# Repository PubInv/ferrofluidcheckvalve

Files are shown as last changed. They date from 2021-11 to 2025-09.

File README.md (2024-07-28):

# A Passive Ferrofluid Check Valve (PFCV)
This repo describes a *passive* ferrofluid one-way valve.
This invention is apparently novel and should be quite important for making it 
easier to fabricate lab-on-a-chip applications, because it has no moving parts,
and is completely passive.

# Theory Paper

For more than a year, I have been trying to develop a complete theory of the valve.
My somewhat messy efforts are [here](https://github.com/PubInv/ferrofluidcheckvalve/blob/master/doc/EnergyMinimization/passiveFerrofluidCheckValveTheory.pdf) in 
this repo. I tend to write expansively in LaTeX, putting down a lot of thoughts and performing calculations more
verbosely than would be accepted in typical published paper.  This paper should be considered my notes at present,
a "treatise" if you will, rather than a paper being prepared for publication. Some parts of it are likely stale.

# Progress as of 13 July 2024

Last night, Joe Hershberge and proved out our best valve design yet. We are 
now consistently getting a collapse pressure of more than 100 cm of water, 
and cracking pressure of less than 10 cm of water.
This is the best ratio we have measured. 
This design used a 3D chamber,
which was a recommendation that Joe made. 

IMG_5257 (1)

Note, in the data below, we used a high-pressure manometer with a resolution of only 4 cmH2O;
we have a more precise low-pressure one, which we will use in the next experiments.
| Trail Name  | Cracking (cmH2O)  | Collapse (cmH2O)  |  Comment |   |
|---|---|---|---|---|
| X1  | 8 | 114  |   |   |
| X2  | 8  | 110   |   |   |
| X3  | 8  | 110  |   |   |
| X4  | 12  |  106 |   | 2" magnet instead of 1"  |
| X5  |  8 |  110 |   | System held upside down in same configuration  |

  I now believe this a very significant result (in this small technical niche which we created.)

# A Humorous History
Our previous attempts to do this were deeply flawed (see below).

When public invention volunteer Veronica Stuckey agreed to work on this project, 
she invigorated the design effort. I wrote a quick (3-day) simulation using particles
in a magnetic field, which gave me some rough guidance. This allowed
me to design an asymmetric chamber which I thought might work. 
Veronica immediately tested it, and it worked---but in the opposite direction from the
way that I thought it would work!
That is, my theory of why the inlet would have low cracking pressure and the outlet 
sustain high pressure was completely and perfectly backwards. However, this meant
that despite this error, we had succeeded in creating a functional ferrofluid valve
with no moving parts!
-- Robert L. Read

# The Successful Valve

The current valve is described in [the paper](https://github.com/PubInv/ferrofluidcheckvalve/blob/master/doc/journal-1.2/asme2ej.pdf) in this repo that we will
submit to an open access journal soon. Like all Public Invention inventions, we do not seek patents, and you are free to use this design under the CERN Strong Reciprocal License [(CERN-OHL-S-2.0)](https://ohwr.org/cern_ohl_s_v2.txt). 

The gist of the fundamental invention can be understood from the this diagram:
TopViewFerrofluidModelLabelled

Veronica Stuckey made a [nice video](https://www.youtube.com/watch?v=IGzz6LX1n6A) of her work that explains it well.



# Design For a Piston to Make a Pump

One of the most interesting things to do with these valves are to use them to make a pump. A pump simply requires a change in volume in the 
pumped fluid between two valves allowing flow in the same direction. We demonstrate this with our existing appratus via a hand-pumped syringe.
However, we could also use a ferrofluid piston, in which case we would have a pump with no moving parts except for ferrfoluid itself.

A piston may be made by moving a blob of ferrofluid in channel (this has been done by many researchers already.) Based on some initial
experiments, here is our design for an electronic ferrofluid piston:

Pump Improvements

# Initial (Wrong Polarity) Sketch Idea

NOTE: as mentioned before, this idea is wrong, but usefully wrong---the valve works in the opposite direction to what is suggested.

Ferrofluid Check Valve Idea #2

# Future Steps

As always, Public Invention invites you take this idea and run with it! Some potential fun things to do next would be:
1. Can the performance of the valve be improved by shaping the chamber and/or the magnetic field better?
2. How do the pressures change if you scale it down?
3. How far can it be scaled down with a 3D printer before some sort of lithographic or etching technique is required?
4. Can you make a positive-displacement pump on a single unit by making a 3D printed pump consiting of a 2 PFCVS, a piston made out of a ferrofluid bolus, and an external electomagnet to move the piston (possibly on a PCB)?
5. This design is essentially a 2D shape slightly extrudede to be a 3D volume. Is there a fully 3D design that is similar but would have better performance?

# Previously (2019)
An attempt to build a ferrofluidcheckvalve

This project is now considered a failure; I've attempted to write up what was learned, which is [published](https://medium.com/@RobertLeeRead/failed-experiments-with-ferrofluid-742fa13b0ae1) at Medium

# References

Note: The academic paper herein contains a better list of references!

[Micromachines | Free Full-Text | Magnetically Induced Flow Focusing of Non-Magnetic Microparticles in Ferrofluids under Inclined Magnetic Fields | HTML (mdpi.com)](https://www.mdpi.com/2072-666X/10/1/56/htm)

[Ferrofluidic Pumps: A Valuable Implementation Without Moving Parts | IEEE Journals & Magazine | IEEE Xplore](https://ieeexplore.ieee.org/abstract/document/5196729/citations?tabFilter=patents#anchor-patent-citations)

[Modeling of ferrofluid magnetic actuation with dynamic magnetic fields in small channels | SpringerLink](https://link.springer.com/article/10.1007/s10404-014-1442-7)
(This paper was the one talking about the rotating magnets, however, this was all done in COMSOL simulation)

[Development of a novel electromagnetic pump for biomedical applications - ScienceDirect](https://www.sciencedirect.com/science/article/abs/pii/S092442471000049X)

[Magnets & Magnetism Frequently Asked Questions | Magnet FAQs (intemag.com)](https://www.intemag.com/magnetic-frequently-asked-questions)
(This site I referenced because of the portion the talks about how a magnet's strength drops off over distance, and gives a good overview on magnetic behavior for the uninitiated)

[On demand manipulation of ferrofluid droplets by magnetic fields - ScienceDirect](https://www.sciencedirect.com/science/article/abs/pii/S092540051631913X)
(Ferrofluid behavior with magnets, not specific)

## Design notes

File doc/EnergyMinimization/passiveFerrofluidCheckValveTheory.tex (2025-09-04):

%%%%%%%%%%%%%%%%%%%%%%%%%%% asme2ej.tex %%%%%%%%%%%%%%%%%%%%%%%%%%%%%%%
% Template for producing ASME-format journal articles using LaTeX    %
% Written by   Harry H. Cheng, Professor and Director                %
%              Integration Engineering Laboratory                    %
%              Department of Mechanical and Aeronautical Engineering %
%              University of California                              %
%              Davis, CA 95616                                       %
%              Tel: (530) 752-5020 (office)                          %
%                   (530) 752-1028 (lab)                             %
%              Fax: (530) 752-4158                                   %
%              Email: hhcheng@ucdavis.edu                            %
%              WWW:   http://iel.ucdavis.edu/people/cheng.html       %
%              May 7, 1994                                           %
% Modified: February 16, 2001 by Harry H. Cheng                      %
% Modified: January  01, 2003 by Geoffrey R. Shiflett                %
% Use at your own risk, send complaints to /dev/null                 %
%%%%%%%%%%%%%%%%%%%%%%%%%%%%%%%%%%%%%%%%%%%%%%%%%%%%%%%%%%%%%%%%%%%%%%

%%% use twocolumn and 10pt options with the asme2ej format
%% \documentclass[twocolumn,10pt]{asme2ej}
\documentclass{asme2ej}
\usepackage{amsmath}
\usepackage{graphicx} %% for loading jpg figures
\usepackage{hyperref}   % to set up hyperlinks
\hypersetup{
	colorlinks=true,
	linkcolor=blue,
	citecolor=blue,
	urlcolor=blue,
}
\usepackage[square,numbers]{natbib}

\usepackage{float}

\usepackage{outlines}
\usepackage{enumitem}
\setenumerate[1]{label=\Roman*.}
\setenumerate[2]{label=\Alph*.}
\setenumerate[3]{label=\roman*.}
\setenumerate[4]{label=\alph*.}

\newtheorem{conjecture}{Conjecture}
\newtheorem{corollary}{Corollary}
\newtheorem{theorem}{Theorem}

%% The class has several options
%  onecolumn/twocolumn - format for one or two columns per page
%  10pt/11pt/12pt - use 10, 11, or 12 point font
%  oneside/twoside - format for oneside/twosided printing
%  final/draft - format for final/draft copy
%  cleanfoot - take out copyright info in footer leave page number
%  cleanhead - take out the conference banner on the title page
%  titlepage/notitlepage - put in titlepage or leave out titlepage
%
%% The default is oneside, onecolumn, 10pt, final

\title{A Novel Passive Ferrofluid One-way (Check) Valve Based on Energy Minimization}

%%% first author
\author{Robert L. Read
\affiliation{
  Founder, Public Invention\\
  Email: read.robert@pubinv.org
    }
}

%%% second author
%%% remove the following entry for single author papers
%%% add more entries for additional authors
\author{Veronica Stuckey
  \affiliation{
    Biomedical Engineer, University of Texas at Austin \\
    %%Email:  stuckey002@gmail.com
    }
}

%%% third author
%%% remove the following entry for single author papers
%%% add more entries for additional authors
\author{Joe Hershberger
\affiliation{
  Investigator, Public Invention\\
  %%Email: read.robert@gmail.com
    }
}

\begin{document}

\maketitle

%%%%%%%%%%%%%%%%%%%%%%%%%%%%%%%%%%%%%%%%%%%%%%%%%%%%%%%%%%%%%%%%%%%%%%
\begin{abstract}

This work focuses on a novel passive ferrofluid check valve. The structure is free of mechanical moving parts and is based on a ferrofluid plug in a narrow channel.
Check valves, also known as one-way valves, are devices that allow fluids to move in only one direction primarily to prevent backflow in the system.
The valve returns to stasis (closes) under the influence of a static magnetic field when the pressure on the ferrofluid is less than the magnetic forces of the ferrofluid itself.
Here, we present a simple design for a passive, normally closed ferrofluid check valve consisting of a unique channel-and-chamber geometry, a bolus of ferrofluid, and a static magnetic field.
The flow is determined only by the force differential between the pressure of the fluid in the channel and the magnetic force of the ferrofluid at the intersection of the channel and the chamber

Small pumps and valves enable flow management in microfluidic systems.
A novel passive ferrofluid check valve is presented.
The valve consists of only a
unique channel-and-chamber geometry, ferrofluid, and a stationary
magnetic field.
The flow is determined only by the inlet and output pressure,
and the magnetic field is completely static.
The prototype valve and experimental setup are explained
and performance of the valves cracking and collapse pressure reported.
This initial design can be used for microfluid handling and lab-on-a-chip
applications.

Additionaly we present a theory of operation based on energy minimization
and compare predicted performance to actual performance.
\end{abstract}

%%%%%%%%%%%%%%%%%%%%%%%%%%%%%%%%%%%%%%%%%%%%%%%%%%%%%%%%%%%%%%%%%%%%%%
\section{To Do}
\begin{itemize}
\item Fully understand the meaning of the Kelvin Force - This should probably be called a magnetophoretic force,
  or an inverse-magnetophoretic force. It should probably not be called the Kelvin force of the magnetic buoyancy.
  Perhaps we should call it energy minimization buoyancy force.
\item Improve Proof of 2D Manetostatic Blob Minimimization Conjecture
\item Understand Ferrofluid Spikes (a version of Rayleigh-Taylor or (normal-field instability) instability )
\item Prove that theorem that a U-tube cannot make an assymetric valve (yes it is called a U-tube)
  U-tubes obviously make pressure gagues, and this is not dependent on the relative areas,
  though the scale is.
\item Centrifugal force is $ F = m \omega^2 \rho$, where $\rho$ is the distance from the center of the rotating frame of
  reference. So we can make a perfectly linear force in that way.
\item Get magnetohydrodynamics by Rosenweig - $250: https://www.amazon.com/Ferrohydrodynamics-Dover-Books-Physics-Rosensweig/dp/0486678342 There is a Kindle Edition for $20, I should probably buy.
  \item ABSOLUTE MUST: Formulate and prove the perpendicular ferrofluid boundary theorem.
\end{itemize}

\subsection{Writing ToDo}

\begin{itemize}
\item This may be a useful reference: \url{https://hal.science/hal-03416758/document}
\item This is a pump that uses a plug and two check valves: \url{https://www.researchgate.net/publication/37423698_A_ferrofluid_micropump_for_lab-on-a-chip_applications/figures?lo=1}
  \item Write a new section on U-tube theory. Should I use a pen?
  \end{itemize}

\section{Outline}

\begin{outline}[enumerate]
  \1 Introduction
  \1 Theory of magnetostatic blobs and constant and non-constant fields
     \2 Cracking / Collapse
     \2 Two chambers with ferrofluid in a magnetic field
  \1 2D Valve in a chamber
      \2 Veronica's result
      \2 Informal Theory
      \2 Math
      \2 Performance of 2D valves
  \1 3D case
      \2 Math
      \2 3D valve perfomance
  \1 Scaling
       \2 Math
  \1 Conclusion and Future Work
       \2 Scale down
       \2 Improve performance
       \2 Cooling, pumping
\end{outline}

\section{Introduction}

Ferrofluid can be manipulated by electronically controlled
fields to exert force on fluids\cite{torres2014recent,kole2021engineering,ozbey2015modeling}.
This makes it possible to build pneumatic or hydraulic
devices, perhaps on very small scales,
such as a single chip\cite{yamahata2003ferrofluid,hatch2001ferrofluidic}, to
miniaturize fluid handling.
This has been proposed for biomedical purposes\cite{michelson2019novel}
that would use water or body fluids,
although this paper reports only on experiments done with air.
Miniature pumps and valves could be used to make a “lab on a chip” (LOC) or
even to heat or cool different chip areas.

A fundamental component of such
devices is the {\em check} or one-way valve.
Two check
valves on either side of a chamber whose volume can vary creates a
positive displacement pump.
A perfect check valve opens or
{\em cracks} with minimal pressure on the inlet side and sustains maximal
pressure on the outlet side before {\em collapse},
allowing fluid to flow in only one
direction. Following\cite{hartshorne2004ferrofluid} we call the maximum pressure
differential the valve can resist in the direction it is intended to
check or block (from outlet to inlet) the {\em sustainable} or {\em collapse} pressure.

This article is a brief report on an initial but functioning design of a
passive ferrofluid check valve (PFCV) that has no moving
parts except for the ferrofluid bolus itself, which is stationary
in normal operation.
By passive, the authors
mean a check valve that functions without changes to the magnetic
field affecting the bolus, whether that field is induced by a
permanent magne t or an electromagnet.
That is, the flow is determined
purely by the difference between the inlet port pressure and the
outlet port pressure.
To our knowledge, no passive
ferrofluid check valve has been previously reported, despite being an
active area of research and despite such a valve having
significant advantages for operation and especially
fabrication over valves with moving parts.

A number of papers report on ferrofluid pumps, focusing in particular
on micropump and lab-on-a-chip applications\cite{ozbey2015modeling,hsu2018biocompatible}.
Many of these papers use
a version of mechanical valve not based on passive
ferrofluid, even though they move a ferrofluid bolus
with a magnetic field.
For example,
a corrugated silicone micro valve\cite{yamahata2003ferrofluid,yamahata2005plastic}
has been reported.
Other researchers use active valves, which require synchronization with
the ferrofluid plug to form a pump,
such as \cite{menz2000fluidic}, which
describes an active {\em T-Valve} with a moving ferrofluid plug, and
\cite{ando2009ferrofluidic} describes a complete fluid pump with valves
that use
active control of a ferrofluid bolus.
At least two additional kinds of active valves, a {\em well valve} and
{\em Y-valve}, have
been described\cite{hartshorne2004ferrofluid}.
Active control is possible because the
action of the plunger or bolus may be synchronized with the opening and closing
of the valves.
Nonetheless a passive valve would be simpler and less
expensive, and would not require knowledge of the timing of the
plunger.

An interesting functional micropump in which the
moving ferrofluid bolus merges with a fixed ferrofluid valve and then
separates on each pumping cycle has been described\cite{hatch2001ferrofluidic},
but is not a one-way valve.

A passive ferrofluid two-way valve with tunable
opening and closing pressure based on magnetic
field strength\cite{paschalis2013novel} has been tested,
but could not be passively used to make a pump.

This paper has not studied the closing pressure of the PFCV, but reports on
the opening (or cracking) pressure (for flow from inlet to outlet) and
sustainable (or collapse) pressure
when the outlet pressure is higher than the inlet side.

\subsection{The 3D Valve of July 2024}

On July 13, 2024, Joe Hershberger and I tested a 3D valve design that produced our
best performance to date, have a $P$ factor of approximately 11.
This valve is depicted in Fig.~\ref{fig:successful}

\begin{figure}[h]
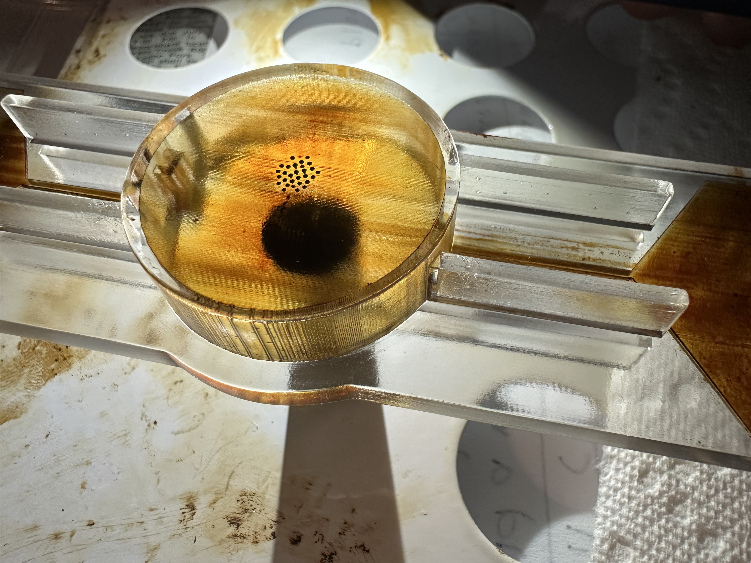
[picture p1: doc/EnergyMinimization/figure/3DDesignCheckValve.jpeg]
\centerline{}
\caption{Successful 3D Valve}
\label{fig:successful}
\end{figure}

The data produced for this valve is depicted in Table~\ref{tab:successful3d}

\begin{table}[]
  \label{tab:successful3d}
  \begin{tabular}{l|l|l|l}
    \hline
    Trial Name & Cracking (cmH2O) & Collapse (cmH2O) &	Comment \\
    \hline
    \hline
     X1 & 8 & 114 &   \\
    \hline
     X2 & 8 & 110  &    \\
    \hline
     X3 & 8 & 110 &    \\
    \hline
     X4 & 12 & 106 & 2" magnet instead of 1"  \\
    \hline
     X5 & 8 & 110 &  System held upside down in same configuration \\
    \hline
\end{tabular}
\end{table}

\section{Passive Ferrofluid Check Valve (PFCV) Design}
%%%%%%%%%%%%%%%% begin figure %%%%%%%%%%%%%%%%%%%
%%% 3.34in is the maximum width you can have for a figure
\begin{figure}
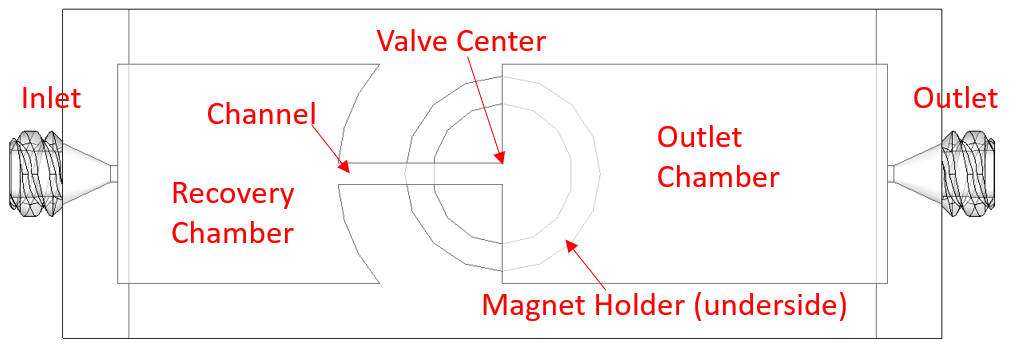
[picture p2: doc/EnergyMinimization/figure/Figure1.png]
\centerline{}
\caption{The passive ferrofluid check valve components}
\label{fig_components}
\end{figure}
%%%%%%%%%%%%%%%% end figure %%%%%%%%%%%%%%%%%%%

The PFCV depicted in Fig.~\ref{fig_components} is a simple asymmetric volume
centered in a magnetic field
which holds a ferrofluid bolus in place.
In the center of a radially symmetric magnetic field
a narrow channel meets a larger open chamber at a right angle.
The ferrofluid bolus is large enough that at rest in the field it
forms a semi-circle in the open chamber. The narrow channel is
longer than the radius of the bolus at rest.
The broad chamber is the outlet side of the valve.
The narrow chamber opens onto a recovery chamber on the inlet
side of the valve.
This design allows the bolus to be recovered from the recovery
chamber when the pressure is equalized if the outlet pressure is
raised above the collapse pressure, driving the bolus away
from the magnetic field.
The PFCV does not resist pressure as well  as a
valve of the same size
made out of moving, solid parts.
That is, the sustainable
pressure it can resist on the outlet side before failing is relatively
low, and pressure required to crack it open and allow flow is
relatively high.
However, it may operate reliably within a range of
known pressures, and thus be sufficient to build a
pump-on-a-chip.
Furthermore, the PFCV reported here is a preliminary design which
can probably be significantly improved.
The authors found the
existence of the PFCV worth sharing immediately.

\section{Method}

The valve depicted Fig.~\ref{fig_components}
was designed using Solidworks 2016.
It is freely licensed via the CERN OHL Strong Reciprocal License\cite{stuckey2021,stuckey2021stl}.
The model consists of a 15mm long, 2mm wide channel, a large outlet
chamber, a recovery chamber,
two female luers, a magnet holder ring and two legs to provide room
for the magnet.  All volumes are 2mm high.
The 3D shape
of the chambers can be thought as a 2mm high extrusion of a 2D shape.
Viewed from the top, one end opens up to a recovery
chamber of circular profile 30mm in diameter and the other
an outlet chamber with a flat wall.
A magnet holder ring 12.7mm inner diameter (1/2'') was created centered on the channel-chamber
junction, below where the bolus is placed, to hold a permanent magnet in place
at the center of the valve. When two magnets are used, the magnet on
top naturally stays in the same position due to attraction to the magnet below.
On the inlet side of the channel
opens into a recovery chamber shaped to allow the ferrofluid to be
passively drawn back into the channel by the magnetic field after a
collapse of the bolus.
The model was printed on a Projet MJP 2500 (3D
Systems, Rock Hill, SC), using Visijet M2G-CL and VisiJet M2 SUP as
material and support respectively (3D Systems, Rock Hill, SC). Support
material was removed by using an EasyClean system (3D Systems, Rock
Hill, SC) and Dawn dish soap (Procter \& Gamble, Cincinnati, OH) to
remove residuals.

%%%%%%%%%%%%%%%% begin figure %%%%%%%%%%%%%%%%%%%
%%% 3.34in is the maximum width you can have for a figure
\begin{figure}
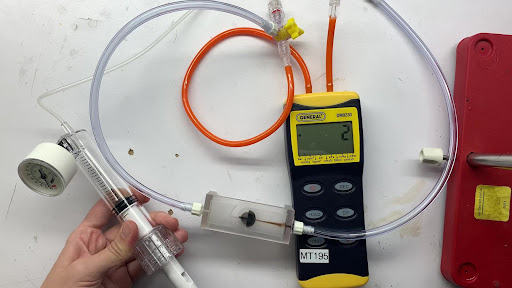
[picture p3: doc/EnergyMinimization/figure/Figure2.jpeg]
\centerline{}
\caption{Equipment set up}
\label{fig_equipment}
\end{figure}
%%%%%%%%%%%%%%%% end figure %%%%%%%%%%%%%%%%%%%

As shown in Fig.~\ref{fig_equipment} and in our demonstration video\cite{stuckey2021video},
a basixCOMPAK 30atm pressurizing syringe (Merit Medical, South Jordan,
UT) is connected to the model via a two-way stopcock (Qosina,
Ronkonkoma, NY), tubing (Natvar, City of Industry, CA), and male
(Injectech, Fort Collins, CO) and female luer (Qosina, Ronkonkoma,
NY), allowing integration of a manometer (General Tools, Secaucus, NJ)
to measure pressure. A 12.7mm x 25.4mm (1/2” x 1”)
cylindrical neodymium magnet (Apex
Magnets, Petersburg, WV) with a pull force of 14.6 kg (32.24 pounds)
was placed inside the magnet channel by means
of a tight fit and 0.2 mL of ferrofluid (Apex Magnets, Petersburg, WV)
was injected into the model using a 3mL syringe (BH Supplies, Jackson,
NJ).

To obtain values, pressure was applied through the pressurizing
syringe, as demonstrated in a video \cite{stuckey2021video}.
Pressure was first applied from the outlet side of the model.
The maximum pressure difference from the outlet side that the
valve can withstand before collapsing, will be referred to as the
sustainable pressure or {\em collapse} pressure.
Pressure applied from the inlet needed to
initiate flow will be referred to as the {\em cracking} pressure.

The cracking pressure was first measured by increasing the pressure
difference on the inlet side until flow is initiated (at which point
the valve is ``open'' and
pushing the syringe plunger faster simply increases flow without
increasing the pressure.) Then the
collapse pressure was measured by increasing the pressure
difference on the outlet side. At pressures below the sustainable
pressure, the valve holds pressure well with no observable leaks of
air in the short time (a few minutes) of our experiment. When the
sustainable pressure is exceeded, the bolus explodes violently into
the recovery chamber. When the pressure difference is equalized, the
bolus may passively recover into the central position, or it may need
to be actively “combed” with a magnet back into the central position.

The procedure was performed first with one magnet, named the “Single
Magnet” configuration, placed below the channel-chamber connection.
The “Dual Magnet” configuration was performed with the magnet in the
same position as the Single Magnet case in the same position, but with
a second magnet of the same kind placed vertically on top of the model,
arranged to be strongly attracted to the lower magnet.

\section{Results}
The final pressures obtained demonstrate a clear difference between
the inlet cracking pressure and outlet sustainable pressure, creating
an effective passive check valve.

%%%%%%%%%%%%%%% begin table   %%%%%%%%%%%%%%%%%%%%%%%%%%
\begin{table}[t]
\footnotesize
\caption{Result pressures}
\begin{center}
\label{table_ASME}
\begin{tabular}{|p{0.3in} |p{0.4in} |p{0.49in} |p{0.45in} |p{0.6in} |}
\hline
Magnet configuration &
Cracking Pressure kPa  (mmHg) &
Collapse Pressure kPa  (mmHg) &
Pressure Difference kPa  (mmHg) &
Approx. Ratio: Cracking to Collapse Pressure \\
\hline
Single &
1.1 (8) &
5.5 (41) &
4.4 (33) &
1:5 \\
\hline
Dual &
8.5 (64) &
17.5 (131)&
8.9 (67)&
1:2 \\
\hline
\end{tabular}
\end{center}
\end{table}
%%%%%%%%%%%%%%%% end table %%%%%%%%%%%%%%%%%%%

The ferrofluid had observable differences in behavior between the two
configurations.  After the pressure equalized
following a collapse of the bolus due to
exceeding the sustainable pressure, the single magnet
configuration often repaired itself by drawing the fluid back
into a centered bolus passively.
After a collapse with two magnets, fluid further from the bolus
remained stationary while the fluid closer was pulled back to the
center. Following the removal of the top magnet, the stationary fluid
then began to return to the bolus. This is consistent with the
localization of the magnetic field between two magnets, and the
weakening of the magnetic field further from the channel-chamber
juncture in the dual magnet configuration.

Although the dual magnet configuration demonstrated a larger absolute
pressure difference due to magnetic field strength between the
cracking and the collapse pressure, the single magnet configuration
granted a larger ratio of collapse pressure to cracking
pressure due to the much lower cracking pressure.
The authors conjecture that the low cracking pressure may have
been not only to the weaker magnetic field, but the weakening at the
top of the 2mm high channel, which was further away from the magnet
in the single magnet configuration.

\section{Theory}

In constructing a theory of one-way (check) valves with no moving parts except fluid,
it is perhaps worth starting with some basics, because we are unlikely to
be able to make valve competitive with solid valves on their own terms.

\subsection{Definitions}

A check valve has an {\em inlet port} and {\em outlet port}, and is intend to
allow a fluid to flow from the inlet to the outlet, and prevent a fluid from
flowing from the outlet to the inlet.
A {\em fluid chec kvalve} means one which the only moving part is a fluid, in
contrast to a {\em sold check valve} that has, for example, a ball or a flapper
which moves slightly when the valve opens. A {\em ferrofluid check valve} is one
that uses ferrofluid as its working fluid (NOT the fluid that it valves.)
As is typical of check valves, define the {\em cracking pressure} as the
pressure at which the valve allow flow from the inlet to the outlet.
A {\em passive check valve} is a checkvalve that opens automatically,
as opposed to, for example,  an electronically controlled valve that is
opened by detecting the pressure in the inlet port and the outlet port (a {\em active checkvalve}.)
This paper is about a design for an {\em passive ferrofluid check valve}.
All valves potentially fail when the outlet port greatly exceeds the pressure
on the inlet port. In a solid check valve this pressure difference may be
so high that it not is stated as a performance metric of the valve. This will
not be the case in the passive ferrofluid check valves discussed here.
We call the pressure at which flow occurs from the outlet to the inlet as
the {\em collapse pressure}.

The primary metric that this paper attempts to optimize is the ratio of the
collapse pressure to the cracking pressure, which we call the {\em collapse performance}
of the valve. A higher collapse performance is better.

\subsection{The U-tube As A Thought Experiment}

Consider as a thought experiment the venerable U-tube. When filled with water,
the U-tube acts as a manometer or pressure gauge. Call the arms of the U-tube
$U$ and $V$. As the pressure in $U$ becomes higher than the pressure in $V$,
the water is pushed down in $U$ and rises in $V$. The height of $V$ above
the equilibrium point in centimeters is the gage pressure of $U$ over $V$
expressed in $cmH2O$. In such a simple device the pressure can be literally
measured as the height of a water column, allowing a slight confusion
of the units of length with the units of pressure.
Treated as pressure gauge, it can measure a pressure
no higher than the height $H$ of the equilibrium point of water above the
bottom of the ``U'', since if the water in the $U$ arm is pushed down
to this point, it will continue and bubble away out the $V$ arm, which
will not cause the $V$ arm to rise any further.

Now, let us consider the U-tube as a passive fluid check valve.
It will be a miserably low-performing valve. If we consider $U$ as
the inlet point, the cracking pressure will be $H$. Being completely
symmetric, the collapse pressure will also be $H$, hence the collapse
performance will simple be $\frac{H}{H} = 1$. There seems to
be no way practical way to build a U-tube like fluid check valve.

If we allow the fantastic idea that the U-tube reaches hundreds of time
higher than the Earth's diameter above the
planets surface, and that $H$ is about the diameter of the Earth,
then the gravity field will not be constant, but will
be slowly decreasing with altitude. However, once again the system
is completely symmmetric, so long as the area of the $U$ arm is the same
as the $V$ arm. If, however, the area of the $U$ arm were 100 times higher
than the area of the $V$ arm, the cracking pressure would be less than
the collapse pressure. To calculate precisely how much, we would have to
use calculus to integrate over the gravitational field.
Qualitatively, however, it is easy to see that it would take much less pressure
than $H$ to cause the valve to crack open, since gravity would pull down harder
on the water in the $U$ arm, which would force the water in the $V$ arm
100 times farther away from the surface of the Earth.
Once the water gets very high, it is already in a weak gravitational field.
The cracking pressure would be something grealy
Howewver, adding pressure to $V$ arm would cause the level of the $U$ arm
to rise only 1/100th as much, so the gravitational field would barely
be affected, and the collapse pressure would be something a little less than $H$.
By using a non-constant field, we could create a performant passive fluid check valve.

\section{Other}

Let us consider an ideal blob of ferrfoluid.
\begin{itemize}
\item Assume that a blob in this section means an ideal 2-dimensional blob,
approximated by a blob constrained into a very thin plane.
\item Assume that the B-field is purely perpendicalur to this plane,
and that it completely dominates the magnetism induced in
the ferrofluid itself.
\item Assume that all forces of viscosity and surface tension may
  be ignored.
\item Although we will not model the forces that make it so,
  we will assume that blob of ferrofluid is self-connected and
  will not split into more than one blob.
\item The blob is perfectly incompressible, and so
  has an absolutely unchanging area.
\item The magnetic particles are evenly distributed in the
  fluid no matter what the magnetic field, so that the potential
  energy in the fluid by being in the field depends only on the
  strength of the field.
\item We need not treat the motion, velocity, or inertia of
  our fluid in any way.
\end{itemize}
Under suitable assumptions, we can state two drastically
simplifying assumptions.

\begin{conjecture}[Magnetostatic Blob Minimization]
  \label{conj:mbf1}
  The magnetostaic force on an ideal 2-dimensional blob
  acted upon by a perpendicular magnetic field
  tends to minimize the potential energy in the blob
  and this occurs when its surfaces are in equal strength fields.
  Equivalently, every surface of a blob at rest with no outside
  forces is a line of equal field strength and all surfaces are equal.
\end{conjecture}

\begin{proof}
  Suppose there existed two pixels of the blob near the boundary,
  such that one pixel was occupied by ferrofluid and had a lower
  B-field magnetism than a pixel that was not occupied by ferrofluid.
  The potential energy of this configuration would be higher than
  if the fluid moved from the occupied pixel to the unoccupied pixel.
  Since the fluid will minimize potential energy, all boundaries
  will adjust themselves to have the same field strength.
  \end{proof}
If the area is expanding the blob, it always decreases potential
energy. If the area is contracting the blob, it always increasing
potential energy. However, since the B-field at the two (or more)
surfaces may be different, there may be a force exerted on the
blob. In particular, we are interested in the force exerted on
the blob counterbalancing the force exerted on by fluid pressure
of non-ferrofluid at the surfaces.

Now imagine that a we have a monotone decreasing field centered
on the origin which which is not necessarily circular, with
the A region containg a thin tube, and the B region containing
a wide open region. Imagine that the field in B is radially
symmetric, but monotonically decreasing with distrance from
the origin (but not necessarily the same in the region A.)
A force resisting flow from the outlet to the inlet (from B to A)
is equal to the field strength at a point multiplied by the surface
length.
In this scenario, the air pressure on the blob is a function
of the length of the surface, but the magnetostatic force is
also a function of length, so the length cancels out and becomes
irrelevant.
The collapse pressure is therefore the maximum force at any point between the rest position and the origin
(this field is by construction equal on a semi-circular arc.)
The collapse pressure also depends on the field strength
at the point of the surface in A, but this surface has small length,
and therefore contributes little to the sum of the force.

Conversely, the cracking pressure will be minimized by
making the field strength in the region B as low as possible
at the point when the ferrfofuid has been entirely driven into
region A by air pressure from the inlet.

\begin{conjecture}[Magnetostatic Bolus Minimization]
  \label{conj:mbf}
  The magnetostatic force on an ideal 2-dimensional bolus
  acted upon by a perpendicular magnetic field
  is a function only of the derivative of the magnetic field
  intensity integrated over the changeable path.
\end{conjecture}

\begin{proof}
  The potential energy of the bolus in the magnetic field
  is highest where the magnetic field is highest and there is
  no ferrofluid, and lowest when ferrofluid fills the field.
  Since ferrofluid is incompressible and is
  contrived to be in a thin plane, this can be modeled as the
  ferrofluid either being present (low potential energy) or not
  (high potential energy.) This is thus a conservative force field.

  Force done by the magnetic field decreases potential energy.
  Force is the negative derivative of the potential energy.
  At an instant in time, this depends only on the boundary of the
  bolus. A surface patch which is not on the boundary cannot
  instantaneously change, and therefore cannot change the potential
  energy and exerts no force.
 \end{proof}

\subsection{How the Valve Cracks}

It is clear that a blob that has a bubble of non-ferrous fluid inside it
has higher potential energy that the same blob without that bubble.
Furthermore, such a bubble will feel a pressure to move away from
an area of a higher magnetic strength towared an area of weaker magnetic
strength. A bubble could be trapped, but if we assume that our
field decreases monotonically from a central peak, a bubble
will have a path to escape and will do so.
In this scenario a valve will ``crack'' that, is, crack open
allowing a fluid from the inlet to the outlet, as soon as the
non-ferrous fluid crosses a central boundary.

\subsection{Warmp: A Tube in a Bowl}

Let us consider the use of a simple bowl of water with a tube placed
vertically in it as a one-way valve.
Let the tube be inserted to a depth $D$ into the water.
Blowing into the tube, we willl have to overcome a restiance of $D$
centimeters of $H_2O$ pressure. When we exceed that, the valve will
``crack'' open, and the air will pass through, bubble out of the water,
and into the surrounding chamber.

Now suppose that we blow air into the surrounding chamber, which is
cut off from the tube. Water will start to rise up the tube.
This will resist a pressure equal to the height of the tube.
By making the tube very long, we have made a pretty good one-way valve.
The cracking pressure is relatively low, and the ``collapse'' pressure
is relatively high.  Nontheless, this is a simple one-way valve.

This valve has two major disadvantage:
\begin{itemize}
\item It depends on the force of gravity and the vertical orientation
  of the tube.
\item It has to be relatively large. To with stand a collapse pressure
  of 100 cm $H_2O$, it has to be one meter in the vertical dimenstion,
  which is quite large for a modest pressure.
\end{itemize}

We will see that by using a ferrofluid in a magnetic field, we can
build a valve withot these disadvantages.

\subsection{Warmup: A Bolus in A Channel}

A relatively simple problem is to consider a bolus of
ferrofluid in a thin horizontal channel. Let $x$ be the positions of the center of
the bolus on the $x$-axis.
Placing a cylindrical permanent
magnet beneath it at the origin tends to lock the bolus in place,
forming a plug.
If a small amount of air pressure is applied to in the positive direction,
the bolus will
be displaced to in the positive $x$ direction, but will find a
stable point in balance with the forces exerted by the magnet in
the negative $x$ direction.

As the pressure is increased, the bolus will be displaced further
in the positive $x$ direction.
It will reach a point where further displacement does not increase
the force in the negative $x$ direction, and will soon decrease it.
At this point the plug will fail
catastrophically, spraying messily into the channel in the $x$ direction and letting air through.

The magnetic field in the line just above the face of the magnet can be analytically
described by ellpitical integrals, but they are very difficult to work with symbolically,
but easy to calculate numerically.
MagPyLib is a convenient package for doing so.
Figure~\ref{fig:BolusSetup} shows our setup of the problem coordinate,
and Figure~\ref{fig:BoluSetupMagPyLib} shows the same setup in the MagPyLib simulation software.
The $x$ dimesion is the horizontal, left to right dimension.
The field is polarized, which is why it is negative in the $x$ direction, only
the magnitude matters when
operating on a ferrofluid bolus.

By making assumptions, we can
analyze this to obtain closed form solutions which match our
experience and inform more complicated cases.

\begin{figure}[h]
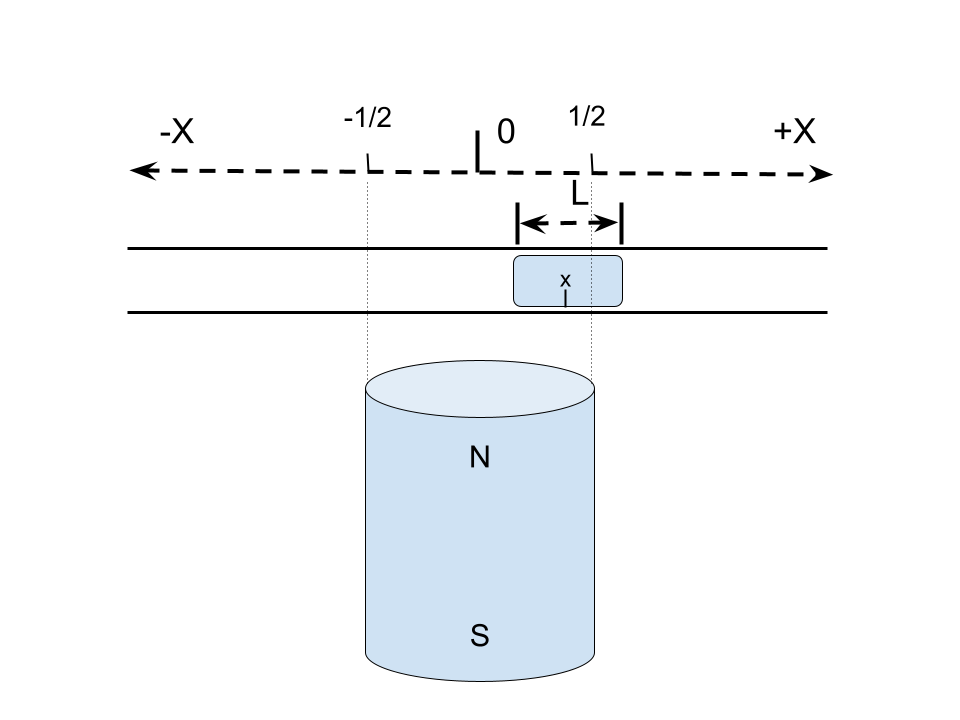
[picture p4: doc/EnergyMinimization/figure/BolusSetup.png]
\centerline{}
\caption{Bolus Coordinate Setup}
\label{fig:BolusSetup}
\end{figure}

\begin{figure}[h]
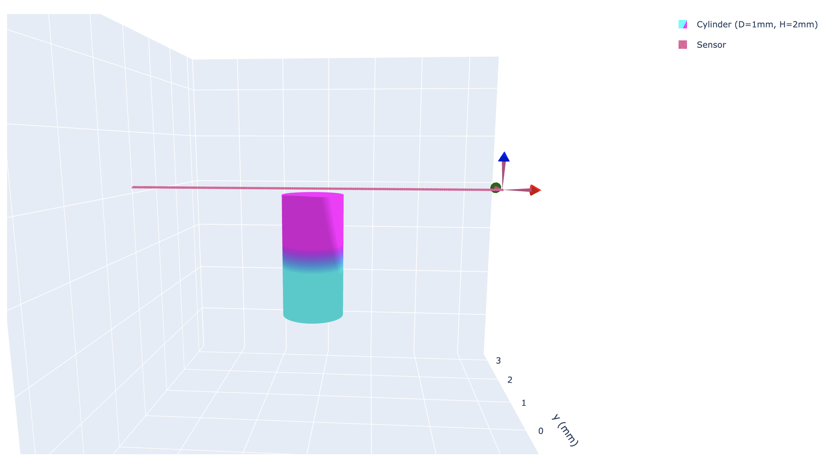
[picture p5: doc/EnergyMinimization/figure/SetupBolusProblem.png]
\centerline{}
\caption{Setup of the Bolus Problem in MagPyLib}
\label{fig:BolusSetupMagPyLib}
\end{figure}

The red line represents the thin channel just slightly above the face of
the magnet.
MagPyLib conveniently computes the field along this line. In particular,
only the $x$ component (the East-West coordinate) of the B-field is relevant to us.
The field was plotted with MagPyLib in Figure~\ref{fig:Bx}.

\subsection{Some synthetic dimensional analysis}

In the work that follows, we have need to relate the ability
of a B-field complete perpendicular to thin plane to exert
force in the plane by virtue of the change in potential energy.

This seems to be beyond my power to define.
As an approximation, we can create a fake unit, the
``planar slope energy'' {\em PSE} unit, which is a factor
which coverts a change (derivative) in the perpendicular B-field intensity
into Pascals (Newtons per square meter).
This artificial constant folds into the nature of the
ferrofluid, the geometry of the plane.

It could be experimentally determined with a manometer
by placing a thin tube of known area in the planar
space above a perpendicular magnetic field
as depicted in the previous section.
If by simulation (such as magpylib) we can know the
maximum slope of the B field in the region of the
thin tube, then the manometer will give us Pascals
at the time of the collapse of the bolus.

We will denote this constant $\Psi$, in memory of Pascal.

(Note: This section assumes it is the slope of the field. I am now not sure of this.)

\subsection{Measuring $\Psi$}

I performed an experiment in a very thin carbon fiber tube. This tube appears
to have a 2mm inner diamter and 3mm outer diameter.

A ferrfofluid plug in this tube placed directly above (and centered) on a
standard 1/2'' x 1'' neobdynium magnet with stuff 280 cm H2O gauge pressure
in suction and 288 cm H2O gauge pressure in compressure. We will estimate
the value of $\Psi$ to be based 284 cm H2O:
\begin{align}
  \Psi =& 284 \text{cm H2O} / 2\text{mm}^2 \pi \\
  \Psi =& 27851 Pa / \pi 3.14159 10^{-6} \text{m}^2\\
  \Psi = 0.0875 \text{N}
  \end{align}

Note that this must be considered ideal. When we used a much larger tube
with a 1/4'' inner diameter, we could only resist 28 to 39 cm H2O.
Sadly more work is required to understand this.

\section{ An Extermely Simple Geometry }
\label{sec:simplegeometry}

It is perhaps surprising that it is possible to make a
passive ferrofluid check valve at all.
This section proves that it is possible by developing
the mathematics as simply as possible in a contrived
but physically realistic configuration.
The principles developed here will be reused with
more efficient geometries later.

\begin{figure}
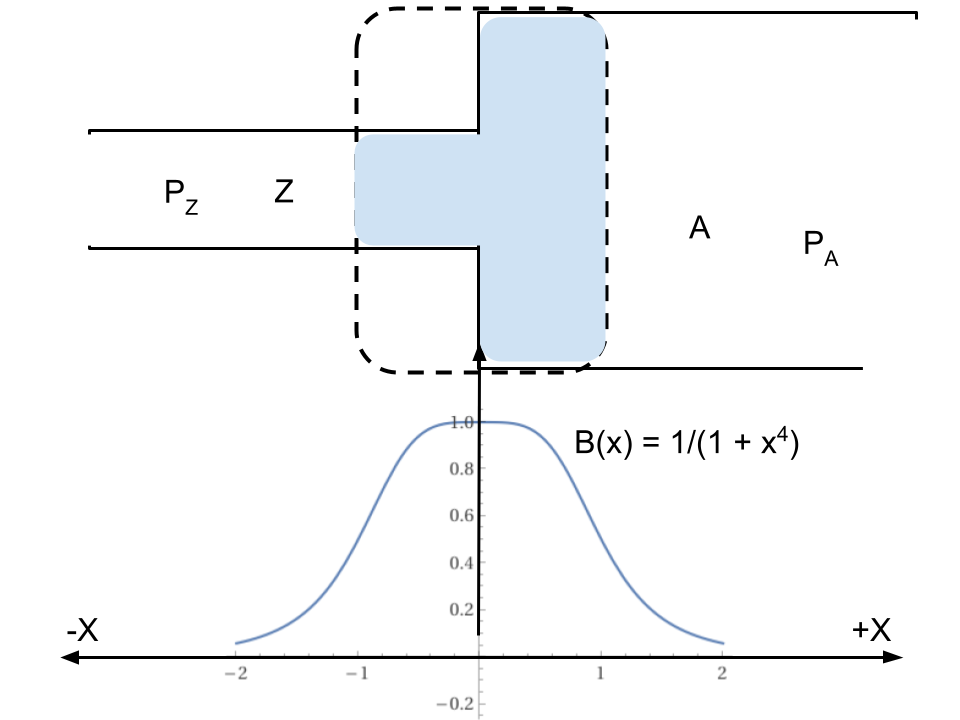
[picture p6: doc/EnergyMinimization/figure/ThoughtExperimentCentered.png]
\centerline{}
\caption{Two centered on a  linear B-field}
\label{fig:centeredthought}
\end{figure}

Consider the thought experiment illustrated in Fig.~\ref{fig:centeredthought}.
Let the $y$ axis be the across across the valve (vertical in our drawing), and
let the $z$ axis be coming out of the page toward the reader (a right-handed coordinate system.)
Imagine that in the $z$ direction the ferrofluid is sandwich between two pieces of glass
so thin that it the whole system may be treated as a 2-dimensional problem.
This allows us to confuse the concepts of volume and area, because the volume
of the bolus will always be proportional to its area.
The heavy dashed line represent the approximate edges of magnet placed underneath
a thin plane contanined between two sheets of glass, constrained by the additional
walls in black. The bolus of ferrofluid is rendered in blue. It creates
two separated chambers, called $A$ (the outlet) and $Z$ (the inlet).
The $A$ chamber is 3 times as high as the $Z$
chamber. The volume of the bolus is chosen so that its area between the glass sheets
is exactly 4 squares of length 1.
That is, there are are 3 squares in the chamber $A$ and 1 in the chamber $Z$.
Let $x_A$ be the position of the interface of area $A$ that fronts the pressures $P_A$.
Because the bolus is contiguous and we have contribed to give it one degree of freedom,
we can use $x_A$ to unambigously represent its postion.  The position of the edge
in the $Z$ chamber is a simple function of $x_A$, which we will denote $Z(x_A)$, which
is a signed negative value.
The $Z(x_A)$ border faces the $P_Z$ pressure. We will treat $P_A$ and $P_Z$ as unsigned values.

The magnetic field intensity $B(x)$ is perpendicular to the thin plane of interest.
We assume the magnet is large enough that $B$ does not depend on the $y$ position.
The formula:
\begin{align}
  B(x) =& \frac{1}{1+x^4}
\end{align}
is observed by inspection with the $B$ field computed to approximately match the shape of the B-field computed
by MagPyLib from a cylindrical magnetic in a line in the plane perpendicular to the magnet axis.
Using this polynomial approximation to a realistic $B$ field allows us to compute the
first and second derivatives, which we will use later.

Assume that the magnetic field is strong enough to keep the bolus everywhere
contiguous with itself (so that there is only one bolus.)
In actually a ferrofluid bolus will exhibit the spikes that is is famous for, but
we will ignore that minor effect,
so that we can
describe the configuration of the bolus only with the positions $x_A$ and $Z(x_A)$.
Since the fluid is incompressible and self-connected and does not very in $y$, there
is only one degree of freedom in its position.
Let $A = 3$,  the height of the $A$ chamber, and $Z = 1$, the height of the $Z$ chamber.
Because the volume is fixed:
\begin{align}
  V = & -Z Z(x_A) + Ax_A \\
  4 = & -Z(x_A) + 3x_A \\
  Z(x_A) = & -4 + 3x_A \\
  x_A = & \frac{4 + Z(x_A)}{3}
  \label{eqn:yvalue}
\end{align}
Thus $x_B$ and $x_A$ are dpendent on each other, and are in fact only one variable.

If we consider geometry qualitatively, we can imagine what will happen
if the pressure is increased from the left or right, perhaps by blowing.
Note that the volume of the bolus is chosen to be about
half the length
of the appreciable magnetic field in this $x$ direction, which is $4$ units.
If the pressure is increased from the right, the bolus will remain intact
and be forced leftward as the pressure increases. If the pressure decreases,
the bolus will move back right ward untill it is centered.
Potential energy in this situation depends only on the position of the bolus,
so the field a conservative mechanical field.

In this model, the narrowness of the plane greatly simplifies the mechanics.
In this simplified model, we can assume
that the potential energy of the magnetic system can be simply
modeled by the presence or absence of ferrofluid at a point in the plane.
The presence of ferrofluid at a point or infinitessimal line ($dx$) decreases the potential energy $U$
of the entire system in proportion to the strength of the field at that position,
and that that strength is describe by our function $B(x)$ where $x$ is the
distance from the origin.
We can thus describe the potential energy as an integral over surface patches $da$:

\begin{align}
  U = \int
\left\{
    \begin{array}{lr}
      B(x)  , & \text{if there is no ferrofluid at } x \\
      0 , & \text{if there is ferrofluid at } x
    \end{array}
\right\} dx
\end{align}

Thus the potential energy is highest when there is no ferrofluid at all,
and lowest when the entire plane is full of ferrfluid.
However, we will generally treat a bolus of fixed volume and assume
that our plane is thin enough that it therefore has a fixed area.

The theory we are developing is a good enough approximation
to allow us to design a valve.
We are furthermore ignoring all effect of the ferrofluid
interacting with itself in terms
of the potential energy.
This is an approximation; ferrofluid famously interacts with itself
by producing ``spikes'' due to field instability.
However, we do rely on the very important property of ferrofluid that
it tends to clump together into a single blob in the presence
of a magentic field.
Furthermore,
we assume the fluid is incompressible,
and therefore always has the volume $V = 4$.
This is true until the bolus collapses; we know that
when it collapses it explodes drastically,
and we do not attempt to model anything after
a collapse event.

If we imagine blowing harder and harder from the right, it is
clear that when the $A$ face of the bolus reaches the origin,
the bolus will explode of {\em collapse} to the left.
This is true because by design $Z =1 $ is shorter than $A =3$, and
so the integral across that line as the same line reflected across
the origin (in the $A$) region will be lower by $1/3$, and the pressure
has obviously been sufficient to overcome $A$.

Since the absolute potential energy of our system is irrelevant,
it will be easier for us to treat the absolute potential energy $U$
as zero when there is no ferrofluid present at all and consider it to go down as ferrofluid is added.
Thus a bolus at rest in a magnetic field has some potential energy which is
less than zero.

Note that pushing the bolus away from its equilibrium
centered on the orign takes a small amount of work.
We imagine an infinite source
of air at pressure, so that we need not worry
about our source air pressure lessening or not being able
to ``do the work'' of pushing the bolus away from equilibrium.
However, note that doing this work
causes the potential energy to increase in the formula below.

In the formuala below, we consider the region piecewise,
broken into the $A$ and $Z$ region.
can reach.
\begin{align}
  U_Z = & -\int_{Z(x_A)}^0 \int_{-\infty}^{\infty}  \Psi Z(x) dy dx \\
  U_Z = & -\Psi\int_{Z(x_A)}^0 Z B(x)  dx  \\
  U_Z = & - \Psi Z \int_{Z(x_A)}^0 B(x)  dx \\
  U_Z = & - \Psi 1 \int_{ -4 + 3x_A}^0 B(x) dx \\
  U_Z = &  \Psi  \int_{0}^{ -4 + 3x_A} B(x) dx \\
  U_Z = &  \Psi  \int_{0}^{ -4 + 3x_A} \frac{1}{1+x^4} dx
\end{align}
\begin{align}
  U_A = &  -\int_0^{x_A} \int_{-\infty}^{\infty} \Psi B(x) dy dx \\
  U_A = &  -\Psi\int_0^{x_A} 3 B(x) dx \\
  U_A = &  -3 \Psi \int_0^{x_A} B(x) dx \\
  U_A = &  -3 \Psi \int_0^{x_A} \frac{1}{1+x^4} dx
\end{align}

Qualitatively, if the bolus is pushed by pressure to the left, the potential energy $U_Z$
goes down, because there is more ferrofluid there, but the potential energy $U_A$ goes up
because there is less ferrofluid in that region. However, if $A$ and $Z$ (the height of our space)
are different, these will change at different rates. If pushed by air pressure from the
right, the region $Z$ actually tugs in the same direction (to the left), but it
will be resisted more strongly by the $A$ region.

\begin{align}
  U = & U_A + U_Z
\end{align}

Due to Thereom~\ref{conj:mbf}, the forces acting on the bolus are purely a function
of the two interfaces $Z$ and $A$.
The force caused by the magnetic field depends solely on the change in potential energy
at each interface, which we have contrived to make two simple lines.
Let the total force in the $x$ direction on the bolus caused by the magnetic
field be $F_M$. Note in Eq.~\ref{eq:magforce} below, the change in potential energy
from the $A$ region will increase (the derivative is negative) and
the change in potential energy will decrease in the $Z$ region.
The partial derivative with respect to $x$ in the $Z$ region is negative, make its contribution
to the force positive (in the $x$ direction), which the contribution to the force
in the $A$ region is negative (in the $-x$ direction.) The force is in Newtons by virtue
of the $\Psi$ coefficient. In fact, we are assuming SI units, but a magnet 3 meters across
is hardly realistic; we can assume scaling to realistic units can be pushed into the $\Psi$
constant for conversion to actual force, and to account for the actual strength of the magnet in Teslas.

\begin{align}
  F_M = & - \frac{\partial U}{\partial x_A} \\
  F_M = &- (\frac{\partial U_A}{\partial x_A} +  \frac{\partial U_Z}{\partial x_A}) \\
  F_M =  & - (- \frac{\partial }{\partial x_A}  \Psi 3\int_0^{x_A} B(x) dx +
  \frac{\partial }{\partial x_A}
 \Psi  \int_{0}^{ -4 + 3x_A} B(x) dx)
  && \text{by substitution} \\
  F_M =  & (3  \Psi B(x_A)  +
  - \Psi \cdot 3 B(-4 + 3x_A) ) && \text{by the Fundamental Theorem of Calculus} \\
  F_M =  &  \Psi 3 ( B(x_A)  +
   -B(-4 + 3x_A) ) && \text{by substitution} \\
  F_M =  & \Psi 3 (\frac{1}{1+x_A^4}  +
    \frac{-1}{1+(-4 + 3x_A)^4}  ) && \text{by substitution}
  \label{eq:magforce}
\end{align}

\begin{figure}
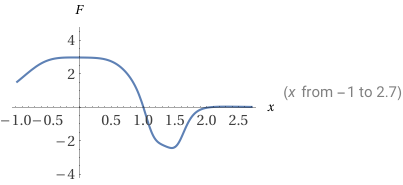
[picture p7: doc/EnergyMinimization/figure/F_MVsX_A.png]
\centerline{}
\caption{Magnetic Force on Bolus as a function of $X_A$}
\label{fig:forceVsX_A}
\end{figure}

Now we have an expression for $F_M(X_A)$ as a function of $x_A$,
which is graphed in Fig.~\ref{fig:forceVsX_A}.
Note first that $F_M(1) = 0$, as we would hope---this is when
the bolus is in equilibrium. It is ``centered'' in the magnetic
field, and as per Theorem~\ref{conj:mbf}, the field at the boundaries
is exactly the same (that is $X_A = 1 \rightarrow Z(x_A) = -1 \wedge
B(1) = B(-1)$.
If the bolus is pushed to the right, $F_M$ becomes negative, meaning
it is pulled to the left by the magnet. If it is pushed to left,
it is pulled to the right by the magnet.

By maximizing $F_M$, we can find the maximum force that the bolus can withstand.
From Wolfram Alpha,
the force on the bolus due to magnetism is maximized at $x \approx -0.12327$
when $F_m = 2.9911 \Psi$. We can predict the bolus will collapse when the
pressure due to $P_A$ exceeding $P_Z$ is $P_A A = 3 P_A$ Newtons, or
nearly $\Psi$ Pascals.

The shape of  $F_M$ has flattish region near the maximum. In practice,
when the bolus reaches this point, the pressure, which is assumed to
be unabated by the increase in volume in the change $A$, will quickly
push the bolus completely into the $Z$ region. This creates a drastic
``spurt'', which is catastrophic on the minor scale of the valve.
The ferrofluid spurts audibly down the $Z$ region. We always
add a chamber to our valves that open up, releiving the pressure and
allowing the ferrofluid to be recollected after a collapse.
One may conjecture that at some scale air could pass throug the
ferrofluid bolus once it is no long self-magnetized by a strong
field, but in practice in the sub-centimeter scale where we work
we have not observed this.

The cracking pressure cannot be computed this way, because once
air pressure from the left as caused $Z(x_A) = 0$, the bubble will move
out and will be ``pinched off'' and escape.
The cracking open of the valve is not at all violent and does not
disrupt the ferrofluid, because the air is moving into a larger
chamber and can simply bubble through the ferrofluid.
To compute the cracking force, we neeed to compute the force at $Z(x_A) = 0$,
where $x_A = \frac{4}{3}$. Note this is close to not precisely where $F_M(x_A)$
is minimized, which occurs at $x_A = 1.4434$, not $x_A = 1.33333$

At this point, the force is $\frac{-768}{337}  \Psi \approx -2.27893  \Psi$.
To reach this point, the pressure force induced by the pressure from the $Z$
region is $Z P_Z = P_Z $ Newtons, or $P_Z = -2.27893  \Psi$.
Since $|-2.27893| < 2.9911 $, we have constructed an assymetric valve.
We define the {\em performance ratio P} of a passive ferrofluid check valve
to be the ratio of the collapse pressure to the cracking pressure.
\begin{align}
  P = \frac{\text{Collapse Pressure}}{\text{Crack Pressure}}
\end{align}
The performance ratio is apparently independent of $\Psi$ and the strengh
of the magnetic field.
The performance ratio of this valve is $\frac{2.9911}{2.27893} \approx 1.3125$.

Compared to a valve made out of solid steel or plastic, this would be considered
a very poor-performing valve. A solid valve would be expected to have a performance
meaured in hundreds or thousands.
Nonetheless, it is unquestionably a
passive ferrofluid check valve.
It is a novel invention and perhaps not at all obvious that it is possible to make
a one-way valve out of nothing but ferrofluid in a shaped chamber in a magnetic field.

A weakness of the theory in this section is that the
volume of the bolus was chosen somewhat arbitrarily to
make the math and geometry easy to understand.
It provides no insight into if the valve would be more performant
with more or less ferrofluid.

Such a low-performing valve could even be useful in some lab-on-a-chip applictions.
However, the geometry of this section was chosen only for illustration.
The reader can no doubt imagine ways to improve it, as we will explore in the
next sections.

We have measure performance ratios of approximately 10, as described
in Table~\ref{tab:successful3d}.

\subsection{An Informal Explanation of the Theory}

It is valuable to have an informal explanation of why
the valve works.
There are two fundamental insights:
\begin{itemize}
\item a non-magnetic fluid that moves into a chamber with
  decreasing magnetic gradient will ``bubble out'' by following
  the gradient away from the magnet
\item if the geometry of the inlet is such that as
  the ferrofluid is pushed toward the stronger part of the field
  the fluid displaced into the outlet is moved into a strong field,
  it will partially offset the rise in potentially energy.
  In other words, the field in the outlet can act as a
  ``counterweight'' to the displacement of the inlet.
  Conversely, if the displaced fluid in the inlet is in
  a place of a low magnetic field, for example, by being
  far awy from the magnet, it will not balance the force
  needed to remove the outlet fluid from the field,
  thus allowing a high collapse pressure.
\end{itemize}

We might ask, is it possible to build such a valve
using simple water in a gravitational field.
I claim this is not possible under realistic circumstances
because the gravitation field does not vary in practice.

I believe it might be possible to build such a valve
out of water if it were place on the arm of centrifuge,
where centrifugal force varies linearly.
It is difficult to see the value of such a speciallized
situation, which is very far removed from lab-on-a-chip
or related fluid handling situations.

\section{ A More Performant 2D Radial Geometry  }

We reported on an early physical model of the PFCV in a
preprint\cite{stuckeyPreprint}
before we understood the theory presented here.
That model used a cylindrical magnet in a 2D plane using a
geometry similar to the geometry developed in the previous section.

After understanding the theory better and designing a fully
radial geometry and ensuring that our ferrofluid bolus
was smaller than the radius of our cylindrical magnet,
we improved our valve design, creating a radial 2D desgin,
a photograph of which is shown in Fig.~\ref{fig:2dRadial}.
A schematic of this geometry, which can be seen as
a modification of the linear system previously presented,
is depicted in Fig.~\ref{fig:ChannelChamber}.

\begin{figure}
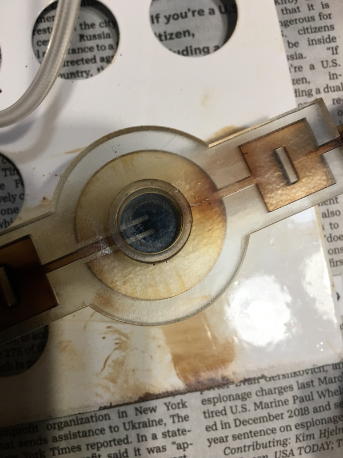
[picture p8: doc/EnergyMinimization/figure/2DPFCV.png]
\centerline{}
\caption{2D Radial PFCV}
\label{fig:2dRadial}
\end{figure}

on the early results as defined here as
reported in Table~\ref{tab:best2D}.

This trial occured at an estimated bolus diameter of
0.355'', or an area of 0.396 square inches.
It was obseverd that if the bolus as as large
as the area of the cylindrical face of the magnet,
the cracking pressure rose drastically, destroying the performance.
This accord with our informal theory: if the edge of the bolus
in the outlet is {\em already} in a weak magnetic field because
it is too large, then it provides no counterbalance, causing the
cracking pressure to rise drastically.

This represents a performance ratio of greater than 7.
\begin{table}[]
  \label{tab:best2D}
  \begin{tabular}{l|l|l|l}
    \hline
    Trial Name & Cracking (cmH2O) & Collapse (cmH2O) &	Comment \\
    \hline
    \hline
     X1 & 8.7 & 62.0 &   \\
    \hline
     X2 & 8.8 & 64.3  &    \\
    \hline
     X3 & 8.9 & 63.5 &    \\
    \hline
\end{tabular}
\end{table}
\footnote{This data was collected with a manometer rated
for low, but which provided more accuracy than in other tables.}

\section{Theory of a 2D Radial Valve}

\begin{figure}
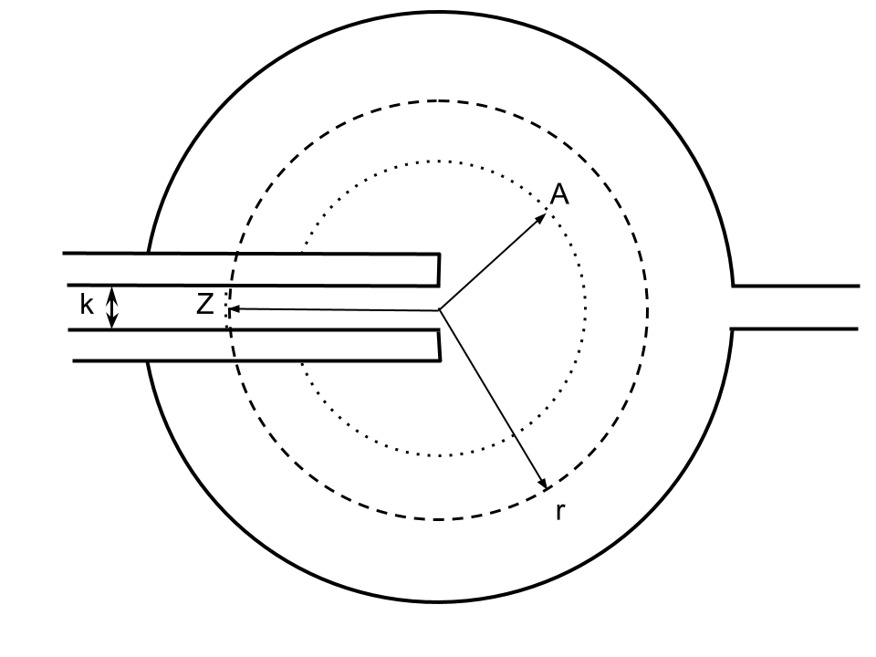
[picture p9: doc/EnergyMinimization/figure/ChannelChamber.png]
\centerline{}
\caption{2D Radial Valve Scheme}
\label{fig:ChannelChamber}
\end{figure}

The 2D radial design, when placed in the radial field created
at the end of a cylindrical magnet, can be seen as a mutation
of the linear valve presented in Sec.~\ref{sec:simplegeometry}.
It greatly increases the surface area in the outlet compared
to the surface area of the inlet, but allowing it to rotate
around nearly the full circumference of a circle.
This geometry forces us to use a polar coordinate system.
However, since it is almost complete radially symmetric,
we will never have to consider the angle in the polar
coordinate system.

The $B$ field of the magnet will be modelled the same
way, but we now think of it as a function of the distance
from the origin,$r$, rather than the $x$ coordinate:
\begin{align}
  B(r) =& \frac{1}{1+r^4}
  \label{eq:cylindricalmagnet}
\end{align}
Note: In Fig.~\ref{fig:ChannelChamber} there are two dashed circles.
The outer circle (heavily dashed) should be thought of as the outline
of the magnet. The dotted inner circle represents the circular edge
of the bolus, whose radius is denoted by $A$.
We used cylindrical magnets 1 inch long and 1/2 inch in
diameter,
We can take the units of $r$ in Eq.~\ref{eq:cylindricalmagnet}
to be in inches.
MagPyLib suggests the field of such a magnet is
actually a little steeper than Eq.~\ref{eq:cylindricalmagnet},
but we will continue to use this.

Our equation of the volume (or area) of the ferrofluid bolus
is now quite different:
\begin{align}
  V = & k r_Z + r_A^2 \\
  r_Z = & \frac{V - r_A^2}{k} \\
  r_A = & \sqrt{V - k r_Z}
  \label{eqn:yvalue}
\end{align}

As before, $r_Z$ and $r_A$ are not independent variables,
and have one degree of freedom between the both of them.

We will typically choose $V$ so that the radius of
the bolus is about $1/2$ of radius of the magnet,
so approximately $1/8$ of an inch, leading
to a bolus area of $\frac{\pi}{64}$ square inches.

We neglect the width of the walls of the channel, which is inaccuracy which should be repaired.

Except for the change in geometry, our analysis is now very similar
to that of the 3:1 chamber analyzed earlier.
The channel potential energy is a two dimensional cartesian integration:
\begin{align}
  U_Z = & -\int_{0}^{r_Z} \int_{-k/2}^{k/2} \Psi B(r_Z) dy dr \\
  U_Z = & -\int_{0}^{r_Z} k \Psi B(r_Z) dr \\
  U_Z = & -k \Psi \int_{0}^{r_Z} B(r_Z) dr \\
  U_Z = & -k \Psi \int_{0}^{r_Z} \frac{1}{1+r^4} dr \\
  U_Z > & -k \Psi \frac{\pi}{2\sqrt{2}} && \text{by evaluation of the integral from $0$ to $\infty$}
\end{align}
But the chamber part is polar integration:
\begin{align}
  U_A = &  -\int_0^{r_A} \int_{-\pi}^{\pi} \Psi r B(r) d\theta dr \\
  U_A = &  -2 \pi \Psi \int_0^{r_A} r B(r) dr \\
  U_A = & - 2 \pi \Psi \int_{0}^{r_A} \frac{r}{1+r^4} dr \\
  U_A = & - \pi \Psi \arctan{r_A^2}
\end{align}
As before, the total potential energy is the sum of these:
\begin{align}
  U = & U_A + U_Z
\end{align}

As before, the force on the bolus is the change in potential
energy. We choose to analyzer this as the change in $r_A$.

By designing an geometry so that $k$ is small, we minimize
the change in potential energy $U_Z$ (and thereby the force) contributed by the
channel. This is especially as the bolus is driven out of the $A$ chamber
and into the $Z$ chamber, because a small change in radius in $A$,
represented by $r_A$, leads to a large change in $r_Z$, since the
fluid is proportional to the square of that radius, and $k$ has been
chosen to be small.  So we can reasonably present that:
\begin{align}
  \frac{\partial U_Z}{\partial r_A} \approx 0
  \label{eq:neglectchannel}
\end{align}

Note: This might NOT be necessary. Possibly I can leave it in please. The integral does
not produce elementary functions, but we are doing to immediately take the derivative of it anyway!

We can construct the force on the bolus the same way, but need to think of a positive
force as the force increasing $r_A$.

\begin{align}
  F_M = & - \frac{\partial U}{\partial r_A} \\
  F_M = &- (\frac{\partial U_A}{\partial r_A} +  \frac{\partial U_Z}{\partial r_A}) \\
  F_M = & \frac{\partial}{\partial r_A} \pi \Psi \arctan{r_A^2} + 0 && \text{ by Eq.~\ref{eq:neglectchannel}}  \\
  F_M = &  \frac{2 \pi \Psi r_A}{r_A^4 + 1} \\
  \label{eq:magforceradial}
\end{align}
This function is maximized at $ r_A = 1/3^(1/4 \approx 0.75984)$, and becomes nearly linear as $r_A$ approaches
$0$.

Howewver, when the pressure in chamber $A$ is high, the area that it can act on decreases as the {\em square}
of $r_A$, which is a critical point. In actual observation, as the presure in $A$ becomes higher
and higher, the bolus is driven further and further into $Z$ and does not collapse unto $r_A$ is near zero.
At any point before collapse, the forces will be in balance, so, using $F_P$ to represent pressure (note $F_P \leq 0$):
\begin{align}
  0 = & F_m + F_P \\
  0 = & \frac{2 \pi \Psi r_A}{r_A^4 + 1} + - \pi r_A^2 P_A \\
   \frac{2 \Psi }{r_A(r_A^4 + 1)} =&   P_A \\
\end{align}
This equation may be solved for $r_A$, but it depends, as we would expect, on $Psi /P_A$
From observation we believe the valve collapses wehn $r_A$ is quite small, approximately $k$.

I am unsure how to proceed. We don't care about $r_A$ when it is greater than about 0.5. If we neglect
the $Z$ regeion entirely, it may be hard to make this balance.

\subsection{Generalizing to Different Geometries}

Let us now suppose that the ferrofluid bolus is three dimensional.
Let us further assume that the shape of the inlet channel and
the outlet channel are both variable, but depend only on the distance
from the center point which we will call the origin of our manetic
field.
The the area of the bolus in the channels $A$ and $Z$ can be expressed
as a function $g_A(r)$ and $g_Z(r)$.

In 3-space, it is probably not the case that we can practically construct a
magnetic field which is purely radially symmetric---which depends solely on
the distance from the origin. However, we may be able to
approximate this. We can certainly construct a field which is
generally monotonic increasing along any ray as it approaches the origin;
a cylindrical magnet with the origin centered on a cylinder face produces
such a field. Producing an analytic integratable function of such
a field is not generally possible, since it involves elliptical integrals.
However, we can either predict or constrain the shape a bolus will take
in 3-space. In free space we can approximate it as a hemisphere centered
on the magnet. In a constrained circular channel it will be a constanst.
In either case we can represent it as a polynomial which we can
tractably anti-differentiate. Let $F_A$ and $F_Z$ be the anti-derivatives
of $g_A$ and $g_Z$, so that:
\begin{align}
  G_A &\int g_A(q) dq \\
  G_Z = & \int g_Z(q) dq \\
\end{align}

We can then use integration by parts our on basic formulae for
for potential energy:
\begin{align}
  U_A = &\int_x^\infty B(q) g_A(q) dq \\
  U_Z = & \int_y^\infty B(q) g_Z(q) dq \\
\end{align}
This can be integrated by parts:
\begin{align}
  U_A = & B(\infty) G_A(\infty) - B(x) G_A(x) - \int_x^\infty B'(q) G_A(q) dq \\
  U_Z = & B(\infty) G_Z(\infty) - B(x) G_Z(x) - \int_x^\infty B'(q) G_Z(q) dq \\
\end{align}
It is clear that $B(\infty) G_A(\infty) = 0$ for any geometry, because even a
sphere feels decrease magnetic force as great distance become zero in the limit.

So:
\begin{align}
  U_A = & - B(x) G_A(x) - \int_x^\infty B'(q) G_A(q) dq \\
  U_Z = & - B(x) G_Z(x) - \int_x^\infty B'(q) G_Z(q) dq \\
\end{align}

If we differentiate this generally we have:

\begin{align}
  \frac{\partial U_A}{\partial x}= & - (B'(x) G_A(x) + B(x) g_A(x ))  -  \frac{\partial }{\partial x}\int_x^\infty B'(q) G_A(q) dq \\
\end{align}
relying on Wolfram alpha to differentiate the improper integral, we have:
\begin{align}
  \frac{\partial U_A}{\partial x}= & - (B'(x) G_A(x) + B(x) g_A(x ))  +  B'(x) G_A(x) \\
  \frac{\partial U_A}{\partial x}= &  - B(x) g_A(x ))
\end{align}

Since $g_A(x)$ is the area and force is area times pressure, the pressure that the $A$ chamber
can withstand is a function {\em purely} of the strength of the $B(x)$. This suggest that we
define the most intense B-field that we can, likely by creating a small air gap.

\subsection{ Connecting Valves in Series to Increase Collapse Pressure of a Gas}

This section added July 27th, 2024.

This section may be out of place, but I wanted to record the math.
We have recently had some succes with our a 3D valve model, obtaining
for the first time a collapse pressure 10 times higher than the cracking
pressure.

In discussion with Prof. David Trevas of Rice University he asked me
if the PFCV could be made stronger by placing them in series.
I suggested that that would not work. But after further thought I
believe it might for gases (though not for incompressible fluids such as water.)

Unlike a flap valve, as the PFCV resists collapse pressure, its
geometry changes and fluid flows toward the (nominal) inlet side.
If that fluid flow decreased the volume of a chamber, the pressure
would rise in proportion to the decreased volume. This would be
``back pressure'' against the ferrofluid blob that is in danger
of collapsing, which would increase the pressure it could withstand.

Of course, if the inlet were simply a fixed chamber, the valve
would have no value. Can we passively improve the collapse pressure?

If we placed two valves in series, then high pressure on the outlet
side would drive some ferrofluid into the interstial space.
This would increase the pressure. This would drive fluid in the second
backing valve out
of the interstial space, somewhat decreasing the pressure.
It therefore behooves us to attempt to build an algebraic model of this
situation to try to understand how much a backing valve might
increase the collapse pressure, if at all.

\begin{figure}
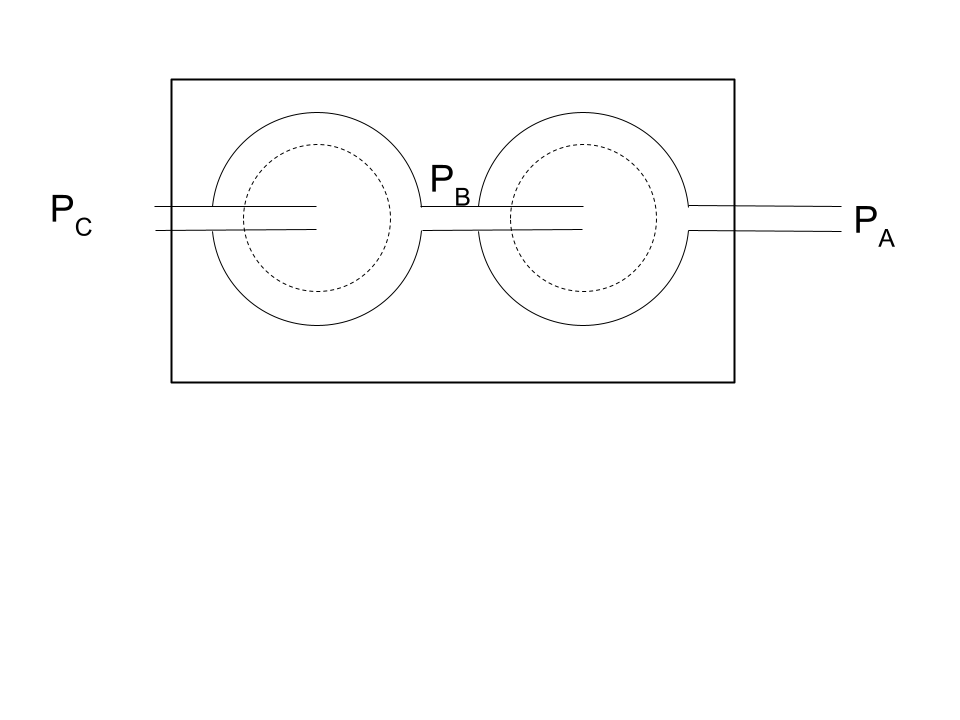
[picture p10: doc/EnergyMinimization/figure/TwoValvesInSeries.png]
\centerline{}
\caption{Two Valves in Series}
\label{fig:Series}
\end{figure}

Define:
\begin{itemize}
\item $V_F$ to be the fixed volume between the valves at rest.
\item $P_C$ to be the valve at the inlet, which for this purpose (resising collapse gague pressure) we can consider ambient pressure.
\item $P_B$ to be the pressure between the valves.
\item $P_A$ to be the pressure at the (nominal) outlet, which when resiting
  collapse would actually be where the fluid goes in if the valve collapses.
\item $V$ be the actual volume between the valves when $P_A \neq P_C$.
\item $D(p)$ be the function mapping the pressure of the valve into
  the displacement of the ferrfluid from the rest state. This is
  only defined when outlet pressure is higher than the input pressure, and
  when the gague pressure is less than the collapse pressure. $D(p)$ has
  been observed to a monotone function. We may approximate it as a
  straight line linear function, even though it probably is not.
  We will treat $D(p) \approx pD$, where $p$ is a pressure, and $D$ has
  units of volume divided by pressure.
\end{itemize}

From Boyle's Law, we have:
\begin{align}
  \frac{P_B}{P_C} = & \frac{V_F}{V}
  \label{eq:boyle}
  \end{align}
We can immediately see that this is not defined if $P_C$ is zero.
In fact in a vacuum we would not expect adding two valve to have any
effect on the ability to resist collapse.

Our fundamental equation models the volume between the
valves, utlizing the incompressiblity of the ferrofluid
\begin{align}
  V = & V_F - D(P_A - P_B) + D(P_B - P_C) \\
  V = & V_F + 2D\cdot P_B - D\cdot P_A - D\cdot P_C \\
    \label{eq:volume}
\end{align}

Combining Equations~\ref{eq:boyle}and~\ref{eq:volume}, and then
using Woflfam Alpha to solve for $P_B$ we have:
\begin{align}
  \frac{P_B}{P_C} = & \frac{V_F}{V_F + 2D\cdot P_B - D\cdot P_A - D\cdot P_C} \\
  P_B = & \frac{ (\pm \sqrt{(-P_A D - P_C D + V)^2 + 8 P_C D V} + P_A D + P_C D - V)}{4 D}
\end{align}

This deserves to be graphed, but we can plug in reasonable values.
If we discover that $P_B$ is relatively high (but certainly less than
$P_A$, we believe it will push back on the bolus by that amount increasing
the collapse pressure of valve complex.

We use cm $H_2O$ as our unit of pressure milliliters as our unit of volume.
We have not measured our bolus size precisely, but I believe them to approximately 1 ml. We have demosntrate collapse pressure of over 100 cm $H_2O$.
A reasonable value for $D$ may be 1 ml per 100 cm $H_2O$.
Typical atmospheric pressure is 14.7 psi, which 1033.512 cm $H_2O$, which
we will approximate as 1000 cm $H_2O$, making $P_C = 1000$.
We set $P_A$ to $P_C + 100 = 1100$.
It is unclear how small we can make the $V_F$ without ferrofluid
from one valve being drawn to the magnet of the other when nearing collapse
conditions. If we imagine that $V_F$ is 4 ml, we have:
$P_B  =  25 (17 + \sqrt{609})\approx 1041.95$. This is a hopeful number!
It suggests that the approach if plaing values in series will work.

\subsection{The Channel-to-a-Chamber}

Our goal, however, is to analyze a somewhat more complicated geometry.
In particular, we are interested in a channel-leading-to-a-chamber,
as depicted in Fig.~\ref{fig:ChannelChamber}.
This geometry was discovered by intuition in attempting to build an asymmetric valve
based on the observed fact that a bubble of air (or any non-magnetic material) will
be pushed out of a bolus by magnetic ``buoyancy'' \cite{wakayama1997magnetic,cheng2014three}.
A less-magnetic material ``floats'' toward the less intense magnetic field inside
ferrofluid. This fact easily observed with a syringe by injecting air into a bolus
in a field.

In that diagram, the edge of the bolus in the chamber is distance $b$ from the
origin. The edge of the bolus in the channel is $a$.
We would ideally like to treat this as a one-dimensional problem as well.
Let us assume once again that a magnetic field is placed at the center
at our diagram (where the channel meets the chamber.)

The most important geometric feature of the channel-and-chamber
valve design is the radius of the cylindrical magnet or magnets
in it. The origin of our plane of operation
will be the center of the top face of the cylindrical magnet,
which is assumed to be beneath the plane, with its North face
in contact with the plane.

The channel is the inlet and the chamber is the
outlet.

Let us assume once again a magnetic field centered on the origin as generated by a
1/2'' by 1'' cylindrical magnet as defined by Equation~\ref{eq:Bfield}.
Since that field is completely radially symmetric, we can use that equation to
describe the B field in the plane, where the parameter of the function
is the distance from the center of the face of the magnet.

In moving to a 2-dimensional representation, we move to polar coordinates
centered at the point the point where the channel and the chamber meet.
Technically, the $B$ field is a field of 3-dimensional vectors; but
by working only in a plane, we treat is as a function of $r$, the distance
from the orgin, and $\theta$, the angle of rotation from the $x$-axis. However,
since the $B$ field is completely symmetric, we can think of it as a one-dimensional
function of distance from the origin $B(r)$. Essentially, we are treating the
$B$ field as the absolute value of the field we treated in the case of the 1-dimensional
bolus.
This can be interpreted as the strength drawing towards the origin, however, since
we deduce everything from this point in terms of change in potential energy,
we need not think of it as signed at all.

The authors had originally hypothesized that the valve would work with a bolus
slightly larger than the radius of the cylindrical magnet.
By experimentation, this was shown to be completely false.
In fact, the desired affect occurs only when the bolus is smaller than the
disc of the cylindrical magnet.

In this interpretation, we can simplify $B(x)$:
\begin{align}
B(x) = &
\left\{
    \begin{array}{lr}
      c(x) , & \text{if } 0 \leq x \leq 1/2 \\
      q(x) , & \text{if } 1/2 < x < 3 \\
      0 , & \text{if } x \geq 3
    \end{array}
    \right\}
    \label{eq:Bfield}
\end{align}

Since we have previously assumed (and it readily observed) that the bolus is a single blob,
at least until it collapses, then we can can relate $a$ and $b$
via the total area of the bolus $S$.
Let us assume that the channel of width $k$ is narrow enough
that the slight arc of the fluid inside the inlet region can be treated as a
straight line.
\begin{align}
S = k \cdot a + \pi b^2
\end{align}
when $a \geq 0$ and $b \geq 0$, so that the areas of $A$ and $B$ are both positive.
(Note: this ignores the small area occluded by the ``walls'' of the channel.
I should probably assign them a width and fix that.)

It is most convenient to measure our position of the bolus, which is
changing shape in this case, as the coordinate $b$, so we we express
$a$ in terms of $b$. Since we will use this algebraic relationship later, we will define it as a function $A$:
This can be solved for $a$:
\begin{align}
  a = & A(b) = \frac{S - \pi b^2}{k} \\
  b_a = & \frac{\sqrt{S - ak}}{\sqrt{\pi}}
  \label{eqn:afromS}
\end{align}

We will later have need of the derivatives of these functions:
\begin{align}
  \frac{d}{db} A(b) = & \frac{- 2\pi b}{k} \\
  \frac{d}{da} b_a = &  -\frac{k}{2 \sqrt(\pi) \sqrt{S - a k}}
  \label{eqn:afromS}
\end{align}

Here $A(b)$ is the value of $a$ as a function of $b$, and $b_a$ is $b$ as a function of $a$.

Note that when $a = 0$, the dependence on $k$ vanishes and:
\begin{align}
  b = & \sqrt{\frac{S}{\pi}} \\
  \label{eq:maximalB}
\end{align}

Since at rest the bolus surface $A$ will be in the same field strength as surface $B$, we can set:

\begin{align}
  B(a) = & B(b) \\
  B(\frac{S - \pi b^2 }{k}) = & B(b)
\end{align}

This can be solved by WolframAlpha (results not incuded here.)
As expected, $ b = a $, that is, both surfaces are equidistant from the
center of our radially symmetric magnetic field.

\subsection{A strategy for computing pressure}

Our fundamental goal is to compute the collapse and cracking
pressure. The collapse pressure is determined by the maximum force needed
to reduce $b$ in the outlet region past some point we will call the
{\em collapse point.}
The cracking pressure is the pressure needed to drive the ferrofluid in the inlet,
represented
by the variable $a$, to the {\em cracking point}, at which point
a bubble forms and is pushed to the outlet.

The check valve we are trying to design will be characterized by
both the collapse pressure and the cracking pressure, but in a single
number the can define the performance of the valve as this ratio $P$,
which we want to be as high as possible:
\begin{align}
  P = \frac{\text{Collapse Pressure}}{\text{Crack Pressure}}
  \end{align}

If the bolus at rest is displaced, the potential energy increases,
moving off a minimum. At a given point, the infinitessimal change
in energy divided by the infinitessimal change in distance
is equal to the force.

If we had a formula for the potential energy as a function of $b$,
we would have a chance of computing this analytically.

In this model,  the narrowness of the plane to simplifies
the problem. In this simplified model, we can assume
that the potential energy of the magnetic system can be simply
modeled by the presence or absence of ferrofluid at a point in the plane.
The presence of ferrofluid at a point or infinitessimal area ($da$) decreases the potential energy $U$
of the entire system in proportion to the strength of the field at a point,
and that that strength is describe by our function $B(r)$ where $r$ is the
distance from the origin (and thus the center of the face of the magnet).
We can thus describe the potential energy as an integral over surface patches $da$:

\begin{align}
  U = \int
\left\{
    \begin{array}{lr}
      B(a)  , & \text{if there is no ferrofluid at } a \\
      0 , & \text{if there is ferrofluid at } a
    \end{array}
\right\} da
\end{align}

Thus the potential energy is highest when there is no ferrofluid at all,
and lowest when the entire plane is full of ferrfluid.
However, we will generally treat a bolus of fixed volume and assume
that our plane is thin enough that it therefore has a fixed area.

We are furthermore ignoring all effect of the ferrofluid
interacting with itself in terms
of the potential energy.
However, we rely on the very important property of ferrofluid that
it tends to clump together into a single blob in the presence
of a magentic field.
We will, in fact, assume that our blob or bolus is perfectly
circular in the chamber,
and a perfect rectangle in the channel. Furthermore,
we assume the fluid is incompressible,
and therefore always has the area $S$.
This is true until the bolus collapses; we know that
when it collapses it explodes drastically,
and we do not attempt to model anything after
a collapse event.

Since the absolute potential energy of our system is irrelevant,
it will be easier for us to treat the absolute potential energy $U$
as zero and consider it to go down as ferrofluid is added.
Since we only model the bolus when part of it is at the origin
in our polar system, we can rewrite our potential energy as negative
and measured against an absolute of zero:

\begin{align}
  U = - \int
\left\{
    \begin{array}{lr}
      B(a)  , & \text{if there is ferrofluid at } a \\
      0 , & \text{if there is no ferrofluid at } a
    \end{array}
\right\} da
\end{align}

Radial symmetry means only the distance from the origin is relevant, so
in fact this is a one dimensional system of the coordinate $b$, which
it is convenent to break into $U = U_N + U_R$,
the channel and the chamber, respectively. We assume that the channel is narrow
enough that we can model the field across the channel as if it is rectilinear.
We can treat these as line integrals:

\begin{align}
  U_R = & -\pi \int_0^b r B(r) dr \\
  U_N = & -k\int_0^a B(r) dr\\
  U = & U_N + U_R = -\pi \int_0^b r B(r) dr  + -k\int_0^a B(r) dr
\end{align}

(This formula for $U_R$ ignores the ``walls'' of the chamber.)
Because pressure applied in the chamber moves the bolus
into the channel, and pressue applied in the channel moves
the bolus into the chamber, the
potential energy changes in both.
The potential energy always goes down as more fluid is added to one side (or
at least never goes up), and thereofore always goes up in the chamber from which it is removed.
The minimum potential energy is a point of balance.
We seek a mathematical description of the
change in totoal potential energy as $b$ changes so
that we can compute the force.
This should allow us to choose $S$ to be most advantageous.
Eventually, this may allow us to design different
magnetic fields to change the performance of the valve.

\subsection{The Collapse Pressure}

Let us define $b_0$ as the value of $b$ when the pressure in the chamber and the channel are equal,
so that the bolus is at rest. This is the point of minimum potential energy.
Let $F(b)$ be the force exerted by the magnet on the bolus at postion $b$.
Then $F(b_0) = 0$.
The potential energy increases as the surrounding gases do work on it (up to the point of collapse
or crack.)
Within that range, the forces are conservative; the potential energy could in theory
be recovered as the bolus spring back to position
if the pressure on the bolus was removed.
Then we have:
\begin{align}
  \frac{d U}{db} =  F(b)
\end{align}

The should allow us to compute the $F(b)$ from $U$.

Let us consider what happens as the outlet gage pressure $P$ is increased.

Qualitatively, we assume that at rest (ambient pressure), the bolus exerts no force. As the
pressure in the chamber increases, the force (the increase in potential energy) will increase
as $b$ is decreased and the bolus is disturbed from its rest position. This force on the
bolus and resiting force exerted by the bolus will increase
as $b$ decreased further from its rest postion. However, eventually this force will cease to
increase and reach its maximum. At that point, the valve will collapse.

The valve is meant to withstand this pressure until a collapse point.
When in balance, the force on the bolus will be zero.
The from on the bolus from air pressure that is attempting to drive the
bolus into the channel will be proportional to $2 \pi b P$, since force is pressure times
area, but in this case the area affected by the pressure is proportional
to the the circumfrence of the bolus (not counting the channel, which is relatively small).
Once this force has pushed much of the fluid into the channel, the inlet-side
bolus boundary will be far away
from the strong magnetic field, and thus may be neglected.
At rest,
he force on the outlet-side bolus boundary $\frac{d U}{db}$ added to the air pressure
force is zero:
\begin{align}
  0 = & 2 \pi b P + - \frac{d U}{db} \\
  2\pi b P = & \pi \frac{d }{db} \int_0^b r B(r) dr \\
  2\pi b P = &  \pi  b B(b)  \\
    P = &  \frac{B(b)}{2}  \\
\end{align}

The position of the bolus $b$ at balance is just proportional $B(b)$.
So the stronger the magnetic field, the higher the collapse pressure.
The strongest magnetic field as at the origin, and in fact we observe the bolus
position be very near the orgin right before the collapse event.

We deduce from this that to build the best possible valve in this geometry,
we should create the strongest possible magnetic field near the origin.

\subsection{The Cracking Pressure}

The cracking pressure $P_r$ will be the force necessary to reach $a = 0$, because at that point,
the non-magnetic fluid will form a ``bubble'' which will be pinched off and displaced into the chamber
by the ferrofluid. This ``bubble'' will be forced in the direction of decreasing magnetic field strength,
because it minimizes potential energy to fill the strong field with ferrofluid preferentially over
non-magnetic fluid. This occurs at $a = 0$, so $A(b) = 0$, or $b = \sqrt{\frac{2S}{\pi}}$ by Equation~\ref{eq:maximalB}.
The force on the bolus inlet boundary does not change as the bolus moves, since $k$ does not
depend on $a$.
The force on the magentic force on the outlet boundary and the inlet boundary
are in fact in opposite directions. The inlet magnetic force resists the cracking
air pressure, and the outlet magnetic force coooperates with it.

In considering the cracking pressure, it is more convenient to track the bolus as a function $a$,
rather than $b$. Thus:

\begin{align}
  \frac{d U}{da} =  F(a)
\end{align}

Then to desribe cracking, we can set the air inlet force in balance with the magnetic force.

\begin{align}
  P_r k = & - \pi \frac{d }{da} \int_0^{b_a} r B(r) dr  + k \frac{d }{da} \int_0^a B(r) dr \\
  P_r k = & - \pi b_a B(b_a) \frac{k}{2 \sqrt{\pi} \sqrt{S - a k}} + k B(a) \\
  P_r k = & - \pi \frac{\sqrt{S - ak}}{\sqrt{\pi}} B(\frac{\sqrt{S - ak}}{\sqrt{\pi}}) \frac{k}{2 \sqrt{\pi} \sqrt{S - a k}} + k B(a) \\
  P_r k = & -  \frac{1}{1} B(\frac{\sqrt{S - ak}}{\sqrt{\pi}}) \frac{k}{2} + k B(a) \\
\end{align}

We can thus create a testable hypothesis that can be verified experimentally by building an appropriate
apparatus. Choosing $k = 10$ and $b_0 = 3/4$, we expect:

\begin{align}
  P = & \frac{\text{Collapse Pressure}}{\text{Crack Pressure}} \\
  P = & \frac{P_c}{P_r} \\
  P = & \frac{\frac{F(b_m)}{\pi b_m}}{\frac{F(\sqrt{\frac{2S}{\pi}})}{k}}
\end{align}

\subsection{Recent Thoughts}

I now believe that we can set up a thought experiment of a bolus
which has two widely separated faces, connected by a thin pipe.
We can design the magnetic field at each end separately.
On the inlet side, we can make the tube 100 times thinner
(in terms of cross-sectional area) than the outlet side.

We can then set up the pressure on the faces as a function
of change in potential energy. However, the factor of 100 will
come into play in the area, but will also mean that a change
in $dx$ on the outlet side will produce a change of $100dx$ on
the inlet side. If the $B(x)$ field magnitude varies as a function
of $x$, this has to be taken into account. This is how the
assymetry is obtained. If $B(x)$ is a constant there will
be no change in force or pressure, and the system will in fact
not resist any pressure at all. However, if $B(x)$ is dropping
off linearly away from the staring position, the counter-balancing
affect of the boundary interfaces will be different, creating the
asymmetry that we observe.

In our actual geometry, the field is of course three dimensional,
but that hardly matters.

\subsection{Conjecture}

Important note: This math strongly suggest that the valve can be
made twice as performant by opening the chamber completely as shown in Figure\ref{fig:360}, so that the
valve is merely a chamber in the center of the bolus.
However, even though we have modeled the fluid as not reacting to itself,
we would not want the ferrofluid itself
to strengthen the field on the inlet side, which might occur. Creating
therefore an arc of someething less than 360 degrees, such as 270 degrees,
or making the walls of the thin chamber very thick, might solve this problem.
\begin{figure}[H]
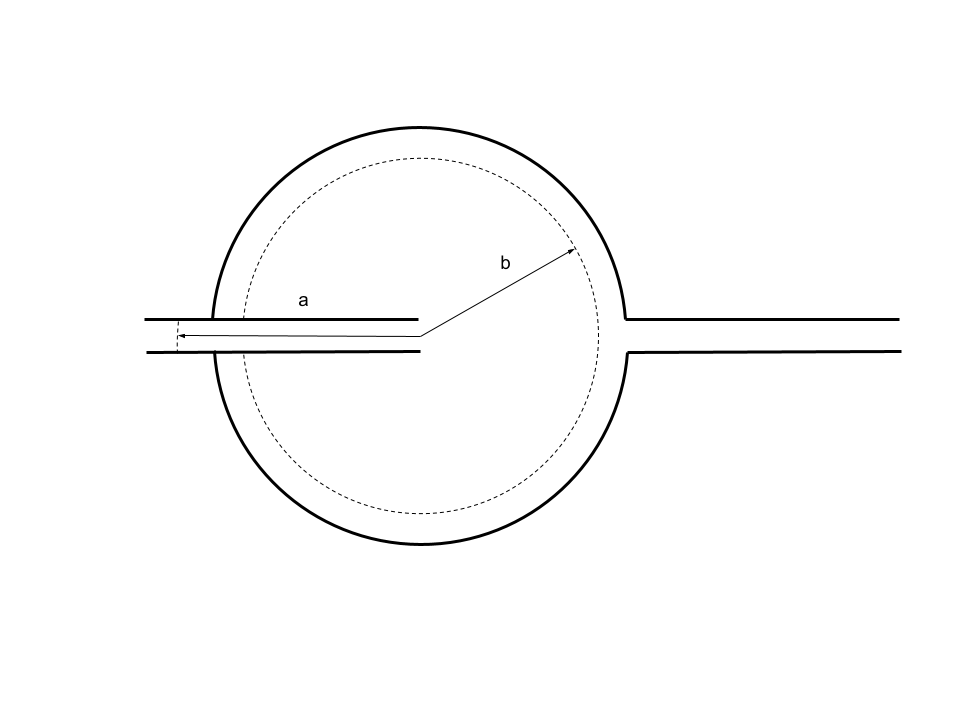
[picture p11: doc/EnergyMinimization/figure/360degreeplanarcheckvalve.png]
\centerline{}
\caption{360 degree planar check valve, an improvement derived from theory}
\label{fig:360}
\end{figure}
This math makes it clear that on the outlet side we want the
bolus surface to be outside a strong field at $r$ to that $r B(r)$ is
maximized to maximize the collapse pressure.
Let us call the value of $b$ that maximizes $b B(b)$ the {\em collapse point.}
We can now see that we want $S$ to be large enough that the edge
of the bolus at rest is beyond the collapse point by some
comfortable margin.

However, to minimize the crack pressure, we want the bolus at rest
in the chamber region inside
the collapse point, because we don't want the inlet pressure to have
to overcome that, even though on the inlet side the length $d$ will
be much smaller that length $\pi b$. However, by the
Magnestatic Blob Minimization principle, this is impossible in a
radially symmetric B field. However, we can build a magnetic field
which is not radially symmetric, thereby improving the performance of the valve.

This suggest that on the inlet side we attempt to make
the magnetic field, only within the channel, as gradual, linear, and
long as possible. This might be possible to accomplish by simply adding
a piece of ferrous metal under the channel, or by making the channel
itself a steel needle. A specially designed magnet or two magnets could be
used. This is somewhat depicted in Fig.~\ref{fig:ifp}.

\begin{figure}
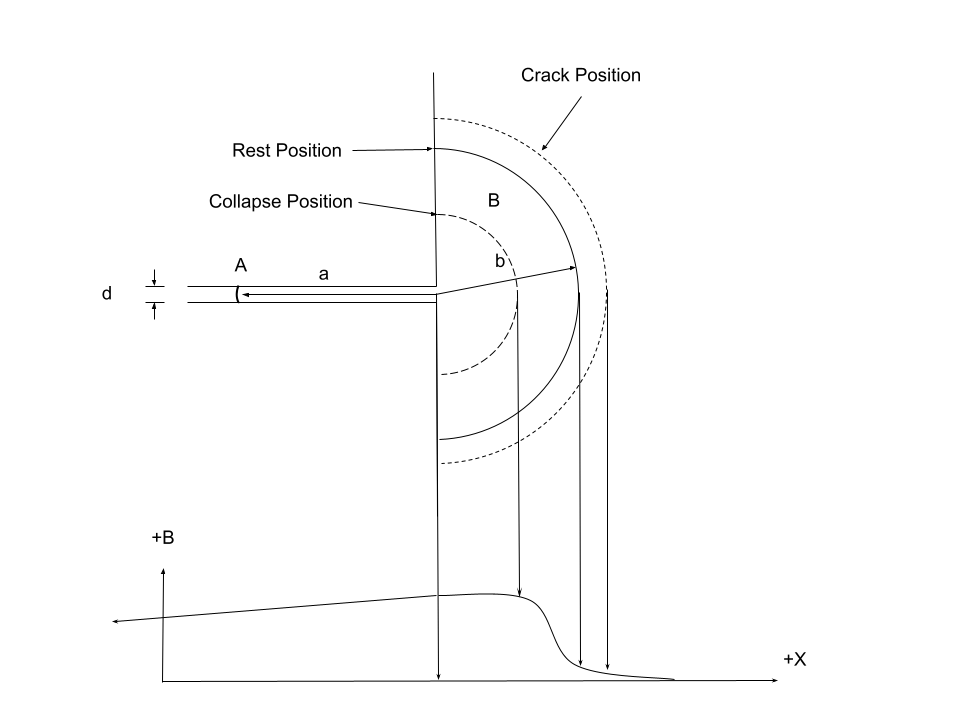
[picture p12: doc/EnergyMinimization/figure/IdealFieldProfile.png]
\centerline{}
\caption{(Rough) Ideal Field Profile}
\label{fig:ifp}
\end{figure}

\subsection{Idea: a 3D version}

It if we had a very powerful and very small dipole, it could in theory
collect a complete sphere of ferrofluid around it. Possibly the tip
of a conical magnet would nearly do this.
In a spherical-like magnetic field, the same principle would
apply, but the added dimensionality would be expected to further
separate the collapse pressure from the crack pressue.

However, a simpler version of this idea based on accessible
cylindrical bar magnets is depicted in Fig.~\ref{fig:3dcheckvalve}.
This has not yet been experimentally tested.

The advantage of having a 3D version predicted by the math is that the area
of the small inlet port would be tiny compared to the area of the spherical
shape. This would tend to produce a very performant valve, if the magnet
field can be designed with sufficient strength. It would seem to be harder
to manufacture in the intended use case of very small valves.

There are two obvious ways to manufacture such a 3D device, both of which require
drilling a small hole into magnet. The first is use a small cylidrical or spherical
magnet. This would be a dipole that could not be approximated as a radially
symmetric field; but it might work anyway.  The second would be to drill a hole
through the axis of a conical magnet. Hopefully the concentration of field strength
at the apex of the magnet would produce a roughly spherical field strength.

Possibly rather than using a sphere, a hemisphere would be more reasonable.

\begin{figure}
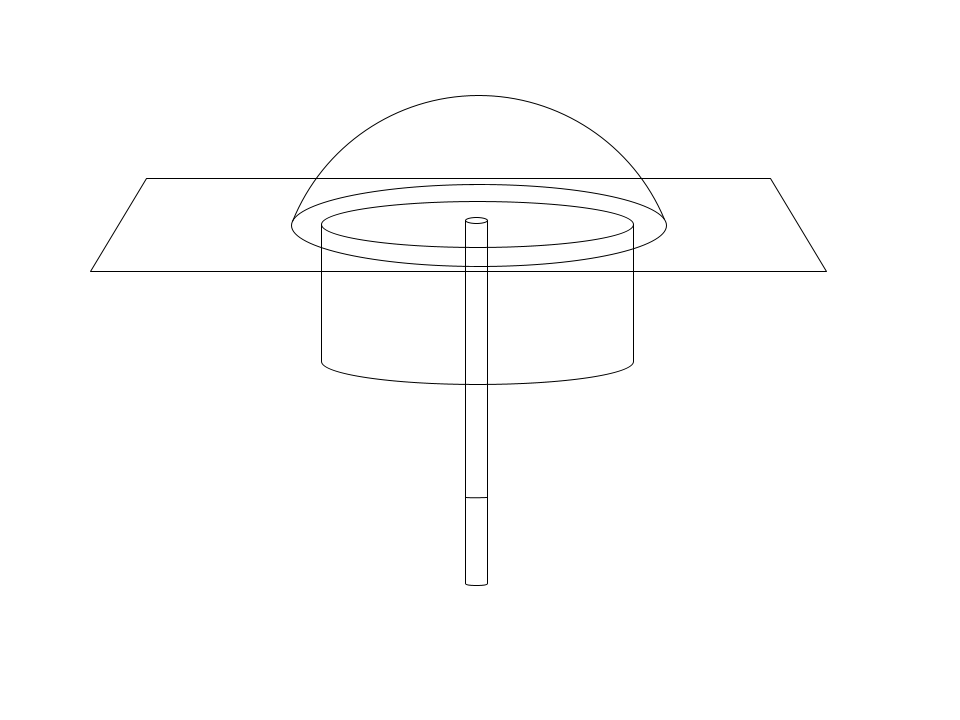
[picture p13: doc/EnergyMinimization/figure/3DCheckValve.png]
\centerline{}
\caption{Untested 3D check valve idea}
\label{fig:3dcheckvalve}
\end{figure}

\subsection{Idea}

We can protect the valve from explosive collapse by using a separate
valve that cracks before the collapse pressure, acting as a ``pop-off''
valve.

\section{Conclusions}

This paper demonstrates an apparently novel passive ferrofluid one-way
valve or check valve (PFCV). This valve is completely passive in that
it depends entirely on the pressure at the inlet port and the outlet
port. The valve has no moving parts (except for the ferrofluid, which
is almost stationary), and a remarkably simple design, consisting of
nothing but a channel, an inlet chamber, and outlet chamber,
and a bolus of ferrofluid in a
static magnetic field.

Although no effort has been made to optimize the design, the pressure
difference between the cracking pressure and the sustainable back
pressure appear great enough to make an effective micropump. The
performance of this one-way valve may improve with additional design
effort; the authors sought to publish this result as soon as it was
observed.  Obvious future research possibilities are:
\begin{enumerate}
\item  To improve the
performance by varying the geometry of the passive design or shape and
strength of the magnetic field.
\item Utilizing this design to make a micro-pump
similar to earlier micro-pumps but with this simpler check valve
design.
\item To provide an explanatory and predictive theory of operation,
for example based on magnetic field strength as per \cite{ando2009ferrofluidic}.
\item Studying the ability of the valve to recover after
  a collapse automatically when high outlet pressure is removed,
  which would increase robustness in some applications.
\end{enumerate}

\section{Possibly Venus for Publishing}

** Consider submitting to this: https://www.sciencedirect.com/journal/journal-of-fluids-and-structures

Read and add this to references:

\url{https://hal.science/hal-01414182/file/2016_marss_mellal.pdf}

%%%%%%%%%%%%%%%%%%%%%%%%%%%%%%%%%%%%%%%%%%%%%%%%%%%%%%%%%%%%%%%%%%%%%%
% The bibliography is stored in an external database file
% in the BibTeX format (file_name.bib).  The bibliography is
% created by the following command and it will appear in this
% position in the document. You may, of course, create your
% own bibliography by using thebibliography environment as in
%
% \begin{thebibliography}{12}
% ...
% \bibitem{itemreference} D. E. Knudsen.
% {\em 1966 World Bnus Almanac.}
% {Permafrost Press, Novosibirsk.}
% ...
% \end{thebibliography}

% Here's where you specify the bibliography style file.
% The full file name for the bibliography style file
% used for an ASME paper is asmems4.bst.
\bibliographystyle{asmems4}

% Here's where you specify the bibliography database file.
% The full file name of the bibliography database for this
% article is asme2e.bib. The name for your database is up
% to you.
\bibliography{ferrofluid}

\end{document}

%%%%%%%%%%%%%%%%%%%%%%%%%%%%%%%%%%%%%%%%%%%%%%%%%%%%%%%%%%%%%%%%%%%%%%
\appendix       %%% starting appendix
\section*{Appendix A: Head of First Appendix}
Avoid Appendices if possible.

%%%%%%%%%%%%%%%%%%%%%%%%%%%%%%%%%%%%%%%%%%%%%%%%%%%%%%%%%%%%%%%%%%%%%%
\section*{Appendix B: Head of Second Appendix}
\subsection*{Subsection head in appendix}
The equation counter is not reset in an appendix and the numbers will
follow one continual sequence from the beginning of the article to the very end as shown in the following example.
\begin{equation}
a = b + c.
\end{equation}

%%%%%%%%%%%%%%%%%%%%%%%%%%%%%%%%%%%%%%%%%%%%%%%%%%%%%%%%%%%%%%%%%%%%%%
\subsection{Second-Level Heading}

The next level of heading is also boldface with upper and lower case letters.
The heading is flushed left with the left margin. The spacing to the next heading is two line spaces.

%%%%%%%%%%%%%%%%%%%%%%%%%%%%%%%%%%%%%%%%%%%%%%%%%%%%%%%%%%%%%%%%%%%%%%
\subsubsection{Third-Level Heading.}

The third-level of heading follows the style of the second-level heading.

%%%%%%%%%%%%%%%%%%%%%%%%%%%%%%%%%%%%%%%%%%%%%%%%%%%%%%%%%%%%%%%%%%%%%%
\section{Use of SI Units}

An ASME paper should use SI units.  When preference is given to SI units, the U.S. customary units may be given in parentheses or omitted. When U.S. customary units are given preference, the SI equivalent {\em shall} be provided in parentheses or in a supplementary table.

%%%%%%%%%%%%%%%%%%%%%%%%%%%%%%%%%%%%%%%%%%%%%%%%%%%%%%%%%%%%%%%%%%%%%%
\section{Footnotes\protect\footnotemark}
\footnotetext{Examine the input file, asme2ej.tex, to see how a footnote is given in a head.}

Footnotes are referenced with superscript numerals and are numbered consecutively from 1 to the end of the paper\footnote{Avoid footnotes if at all possible.}. Footnotes should appear at the bottom of the column in which they are referenced.

%%%%%%%%%%%%%%%%%%%%%%%%%%%%%%%%%%%%%%%%%%%%%%%%%%%%%%%%%%%%%%%%%%%%%%
\section{Mathematics}

Equations should be numbered consecutively beginning with (1) to the end of the paper, including any appendices.  The number should be enclosed in parentheses and set flush right in the column on the same line as the equation.  An extra line of space should be left above and below a displayed equation or formula. \LaTeX\ can automatically keep track of equation numbers in the paper and format almost any equation imaginable. An example is shown in Eqn.~(\ref{eq_ASME}). The number of a referenced equation in the text should be preceded by Eqn.\ unless the reference starts a sentence in which case Eqn.\ should be expanded to Equation.

\begin{equation}
f(t) = \int_{0_+}^t F(t) dt + \frac{d g(t)}{d t}
\label{eq_ASME}
\end{equation}

%%%%%%%%%%%%%%%%%%%%%%%%%%%%%%%%%%%%%%%%%%%%%%%%%%%%%%%%%%%%%%%%%%%%%%
\section{Figures}
\label{sect_figure}

All figures should be positioned at the top of the page where possible.  All figures should be numbered consecutively and centered under the figure as shown in Fig.~\ref{figure_ASME}. All text within the figure should be no smaller than 7~pt. There should be a minimum two line spaces between figures and text. The number of a referenced figure or table in the text should be preceded by Fig.\ or Tab.\ respectively unless the reference starts a sentence in which case Fig.\ or Tab.\ should be expanded to Figure or Table.

%%%%%%%%%%%%%%%%%%%%%%%%%%%%%%%%%%%%%%%%%%%%%%%%%%%%%%%%%%%%%%%%%%%%%%
%%%%%%%%%%%%%%%% begin figure %%%%%%%%%%%%%%%%%%%
\begin{figure}[t]
\begin{center}
\setlength{\unitlength}{0.012500in}%
\begin{picture}(115,35)(255,545)
\thicklines
\put(255,545){\framebox(115,35){}}
\put(275,560){Beautiful Figure}
\end{picture}
\end{center}
\caption{The caption of a single sentence does not have period at the end}
\label{figure_ASME}
\end{figure}
%%%%%%%%%%%%%%%% end figure %%%%%%%%%%%%%%%%%%%
%%%%%%%%%%%%%%%%%%%%%%%%%%%%%%%%%%%%%%%%%%%%%%%%%%%%%%%%%%%%%%%%%%%%%%

In the following subsections, I have inserted figures that have been provided by authors in order to demonstrate what to avoid.  In each case the authors provided figures that are 3.25in wide and 600dpi in the .tif graphics format.  The papers containing these figures have been held from production due to their poor quality.

%%%%%%%%%%%%%%%%%%%%%%%%%%%%%%%%%%%%%%%%%%%%%%%%%%%%%%%%%%%%%%%%%%%%%%
\subsection{The 1st Example of Bad Figure}

%%%%%%%%%%%%%%%% begin figure %%%%%%%%%%%%%%%%%%%
%%% 3.34in is the maximum width you can have for a figure
\begin{figure}
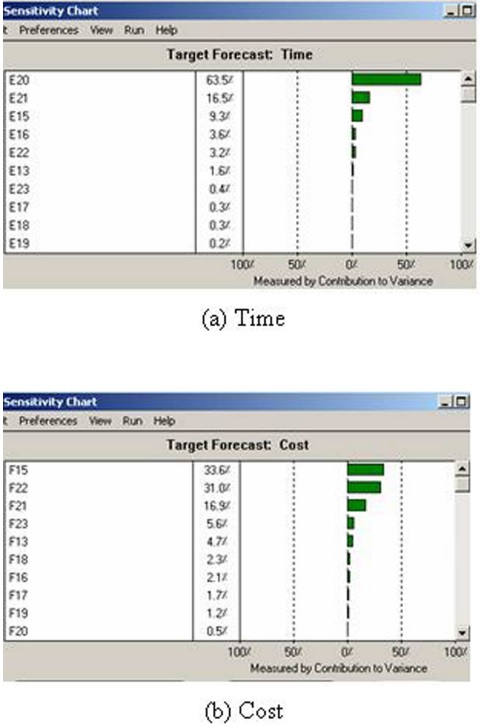
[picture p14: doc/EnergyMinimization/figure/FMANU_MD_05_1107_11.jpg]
\centerline{}
\caption{Example taken from a paper that was held from production because the image quality is poor.  ASME sets figures captions in 8pt, Helvetica Bold.}
\label{fig_example1.jpg}
\end{figure}
%%%%%%%%%%%%%%%% end figure %%%%%%%%%%%%%%%%%%%

In order to place the figure in this template using MSWord, select Insert Picture from File, and use wrapping that is top and bottom. Make sure the figure is 3.25in wide.

Figure~`\ref{fig_example1.jpg}
was taken from a recent paper that was held from publication, because the text is fuzzy and unreadable. It was probably obtained by taking a screen shot of the computer output of the authors software. This means the original figure was 72dpi (dots per inch) on a computer screen. There is no way to improve the quality such a low resolution figure.

In order to understand how poor the quality of this figure is, please zoom in slightly, say to 200\%.  Notice that while the font of the paper is clear at this size, the font in the figures is fuzzy and blurred.  It is impossible to make out the small symbol beside the numbers along the abscissa of the graph.  Now consider the labels Time and Cost. They are clearly in fonts larger that the text of the article, yet the pixilation or rasterization, associated with low resolution is obvious. This figure must be regenerated at higher resolution to ensure quality presentation.

The poor quality of this figure is immediately obvious on the printed page, and reduces the impact of the research contribution of the paper, and in fact detracts from the perceived quality of the journal itself.

%%%%%%%%%%%%%%%%%%%%%%%%%%%%%%%%%%%%%%%%%%%%%%%%%%%%%%%%%%%%%%%%%%%%%%
\subsection{The 2nd Example of Bad Figure}

%%%%%%%%%%%%%%%% begin figure %%%%%%%%%%%%%%%%%%%
\begin{figure}
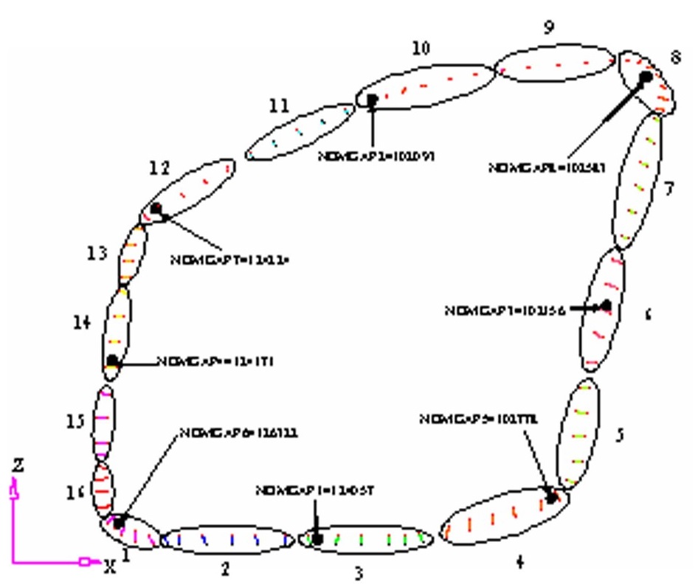
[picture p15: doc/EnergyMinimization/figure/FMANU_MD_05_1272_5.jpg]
\centerline{}
\caption{While this figures is easily readable at a double column width of 6.5in, when it is shrunk to 3.25in column width the text is unreadable. This paper was held from production.}
\label{fig_}
\end{figure}
%%%%%%%%%%%%%%%% end figure %%%%%%%%%%%%%%%%%%%

Figure~\ref{fig_example2.jpg}
demonstrates a common problem that arises when a figure is scaled down fit a single column width of 3.25in.  The original figure had labels that were readable at full size, but become unreadable when scaled to half size.  This figure also suffers from poor resolution as is seen in the jagged lines the ovals that form the chain.

This problem can be addressed by increasing the size of the figure to a double column width of 6.5in, so the text is readable.  But this will not improve the line pixilation, and a large low resolution figure is less desirable than a small one.  This also significantly expands the length of the paper, and may cause it to exceed the JMD nine page limit.  Additional pages require page charges of \$200 per page.  It is best to regenerate the figure at the resolution that ensures a quality presentation.

%%%%%%%%%%%%%%%%%%%%%%%%%%%%%%%%%%%%%%%%%%%%%%%%%%%%%%%%%%%%%%%%%%%%%%
\subsection{The 3rd Example of Bad Figure}
%%%%%%%%%%%%%%%% begin figure %%%%%%%%%%%%%%%%%%%
\begin{figure}
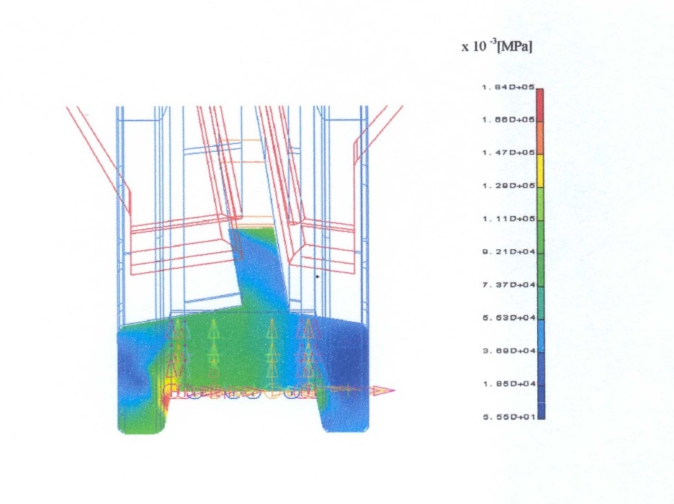
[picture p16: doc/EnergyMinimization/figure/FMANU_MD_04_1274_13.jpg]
\centerline{}
\caption{Another example of a figure with unreadable text.  Even when the paper was expanded to double column width the text as shown in Fig.~\ref{fig_example4.jpg} was of such low quality that the paper was held from production.}
\label{fig_example3.jpg}
\end{figure}
%%%%%%%%%%%%%%%% end figure %%%%%%%%%%%%%%%%%%%

%%%%%%%%%%%%%%%% begin figure %%%%%%%%%%%%%%%%%%%
%%% the maximum width in double column is 6.85in
\begin{figure*}
\centerline{}
\caption{A figure expanded to double column width the text from Figure~\ref{fig_example3.jpg}}
\label{fig_example4.jpg}
\end{figure*}
%%%%%%%%%%%%%%%% end figure %%%%%%%%%%%%%%%%%%%
An author provided the high resolution image
in Fig.~\ref{fig_example3.jpg}
that was sized to a single column width of 3.25in.  Upon seeing the poor quality of the text, the publisher scaled the image to double column width as shown in Fig.~\ref{fig_example4.jpg}
at which point it took half of a page.  The publisher went on to do this for all eight figures generating four pages of figures that the author did not expect. ASME stopped production of the paper even with the larger figures due to the pixilation of the font.

Clearly the text in this figure is unreadable, and it is doubtful that the author can print the output in a way that it is readable.  This is a problem that the author must solve, not the publisher.

As you might expect, I have many more examples, but in the end the author is the best judge of what is needed in each figure.  ASME simply requires that the image meet a minimum standard for font and line quality, specifically the font should be the appropriate size and not be blurred or pixilated, and that lines should be the appropriate weight and have minimal, preferably no, pixilation or rasterization.

%%%%%%%%%%%%%%%%%%%%%%%%%%%%%%%%%%%%%%%%%%%%%%%%%%%%%%%%%%%%%%%%%%%%%%
\section{Tables}

%%%%%%%%%%%%%%%%%%%%%%%%%%%%%%%%%%%%%%%%%%%%%%%%%%%%%%%%%%%%%%%%%%%%%%
%%%%%%%%%%%%%%%%%%%%%%%%%%%%%%%%%%%%%%%%%%%%%%%%%%%%%%%%%%%%%%%%%%%%%%

All tables should be numbered consecutively  and centered above the table as shown in Table~\ref{table_ASME}. The body of the table should be no smaller than 7 pt.  There should be a minimum two line spaces between tables and text.

%%%%%%%%%%%%%%%%%%%%%%%%%%%%%%%%%%%%%%%%%%%%%%%%%%%%%%%%%%%%%%%%%%%%%%
\section{Citing References}

%%%%%%%%%%%%%%%%%%%%%%%%%%%%%%%%%%%%%%%%%%%%%%%%%%%%%%%%%%%%%%%%%%%%%%
The ASME reference format is defined in the authors kit provided by the ASME.  The format is:

\begin{quotation}
{\em Text Citation}. Within the text, references should be cited in  numerical order according to their order of appearance.  The numbered reference citation should be enclosed in brackets.
\end{quotation}

The references must appear in the paper in the order that they were cited.  In addition, multiple citations (3 or more in the same brackets) must appear as a `` [1-3]''.  A complete definition of the ASME reference format can be found in the  ASME manual \cite{asmemanual}.
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

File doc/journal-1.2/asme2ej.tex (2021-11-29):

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

%%% use twocolumn and 10pt options with the asme2ej format
\documentclass[twocolumn,10pt]{asme2ej}

\usepackage{graphicx} %% for loading jpg figures
\usepackage{hyperref}   % to set up hyperlinks
\hypersetup{
	colorlinks=true,
	linkcolor=blue,
	citecolor=blue,
	urlcolor=blue,
}
\usepackage[square,numbers]{natbib}

%% The class has several options
%  onecolumn/twocolumn - format for one or two columns per page
%  10pt/11pt/12pt - use 10, 11, or 12 point font
%  oneside/twoside - format for oneside/twosided printing
%  final/draft - format for final/draft copy
%  cleanfoot - take out copyright info in footer leave page number
%  cleanhead - take out the conference banner on the title page
%  titlepage/notitlepage - put in titlepage or leave out titlepage
%
%% The default is oneside, onecolumn, 10pt, final

\title{A Novel Passive Ferrofluid One-way (Check) Valve}

%%% first author
\author{Veronica Stuckey
  \affiliation{
    Biomedical Engineer, University of Texas at Austin \\
    Email:  stuckey002@gmail.com
    }
}

%%% second author
%%% remove the following entry for single author papers
%%% add more entries for additional authors
\author{Robert L. Read
\affiliation{
  Founder, Public Invention\\
  Email: read.robert@gmail.com
    }
}

%%% third author
%%% remove the following entry for single author papers
%%% add more entries for additional authors

\begin{document}

\maketitle

%%%%%%%%%%%%%%%%%%%%%%%%%%%%%%%%%%%%%%%%%%%%%%%%%%%%%%%%%%%%%%%%%%%%%%
\begin{abstract}
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

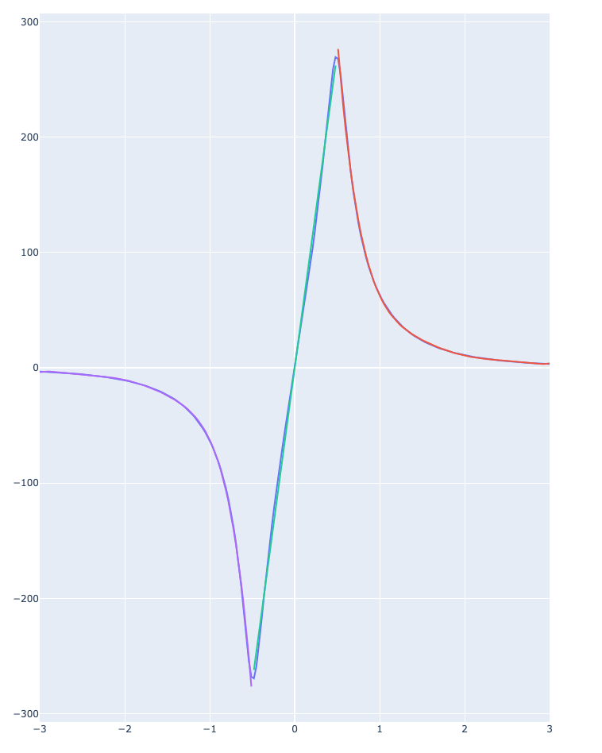
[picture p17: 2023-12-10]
doc/EnergyMinimization/figure/PlotOfBxWithPieceWiseInterpolation.png

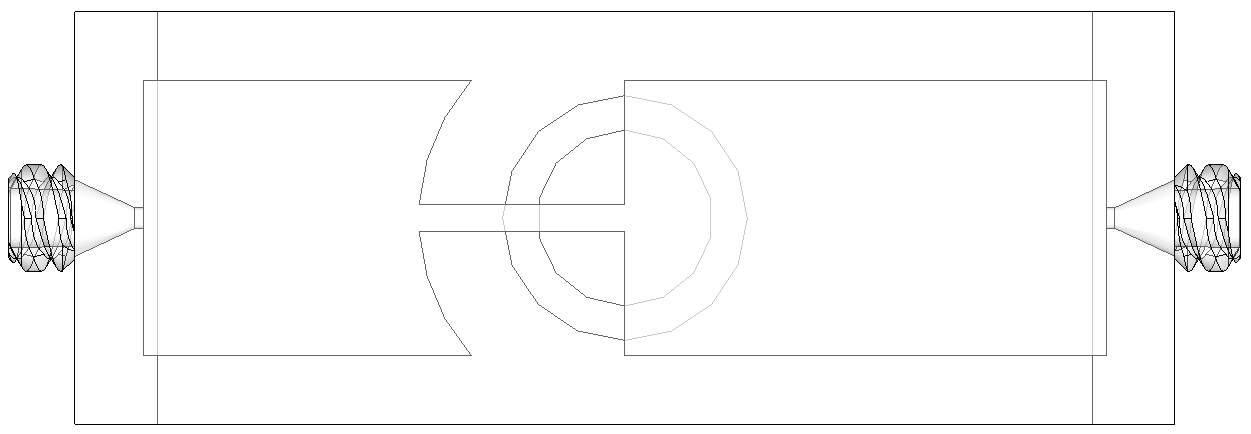
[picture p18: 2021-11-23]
doc/EnergyMinimization/figure/top_view.PNG

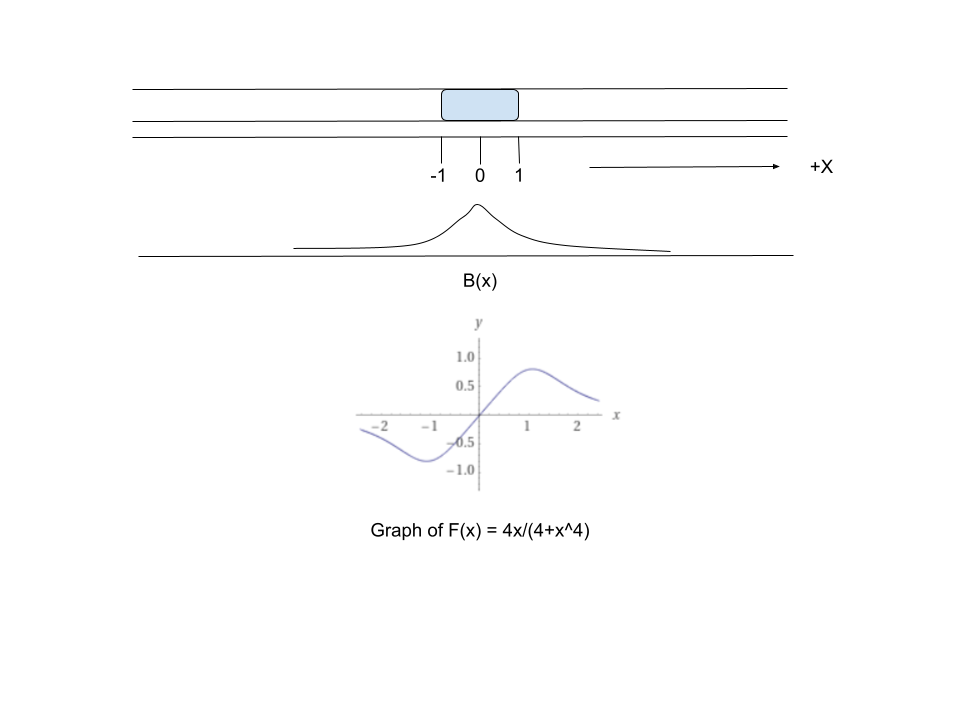
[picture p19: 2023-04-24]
doc/EnergyMinimization/figure/One-dimensionalBolusMath.png

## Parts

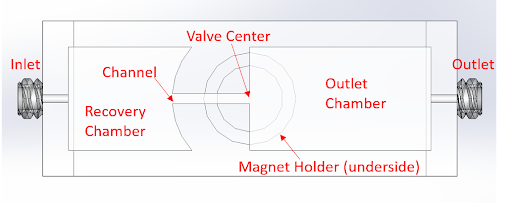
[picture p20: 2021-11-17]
doc/EnergyMinimization/figure/components.png

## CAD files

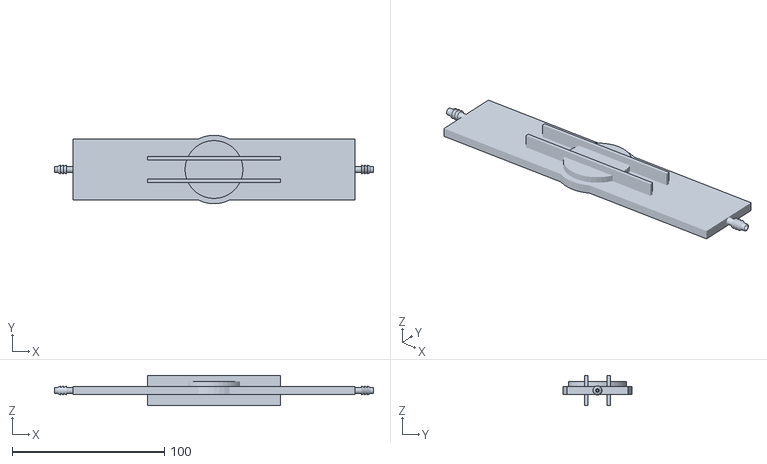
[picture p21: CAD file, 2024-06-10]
model/AirGapValve.stl
209.5 x 45.0 x 20.0

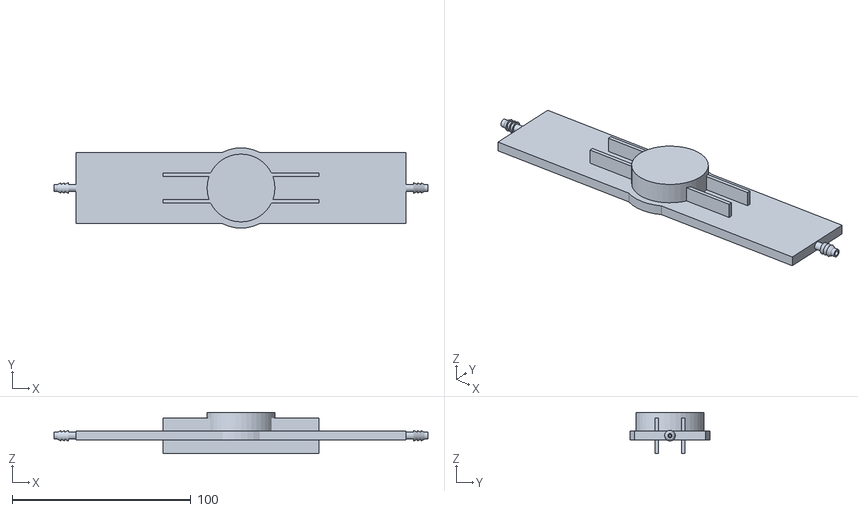
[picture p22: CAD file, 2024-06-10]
model/HighChamber.stl
209.5 x 45.0 x 23.0

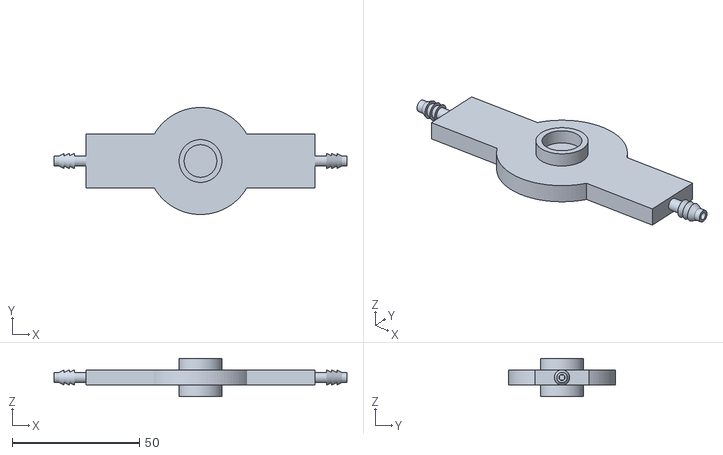
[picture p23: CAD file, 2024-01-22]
model/ImprovedCheckValve3.stl
115.0 x 42.0 x 15.0

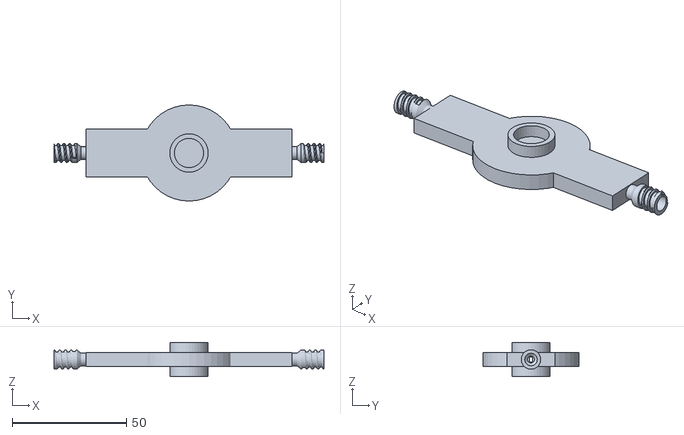
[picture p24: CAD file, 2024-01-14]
model/ImprovedCheckValveV2.stl
118.0 x 42.0 x 15.0

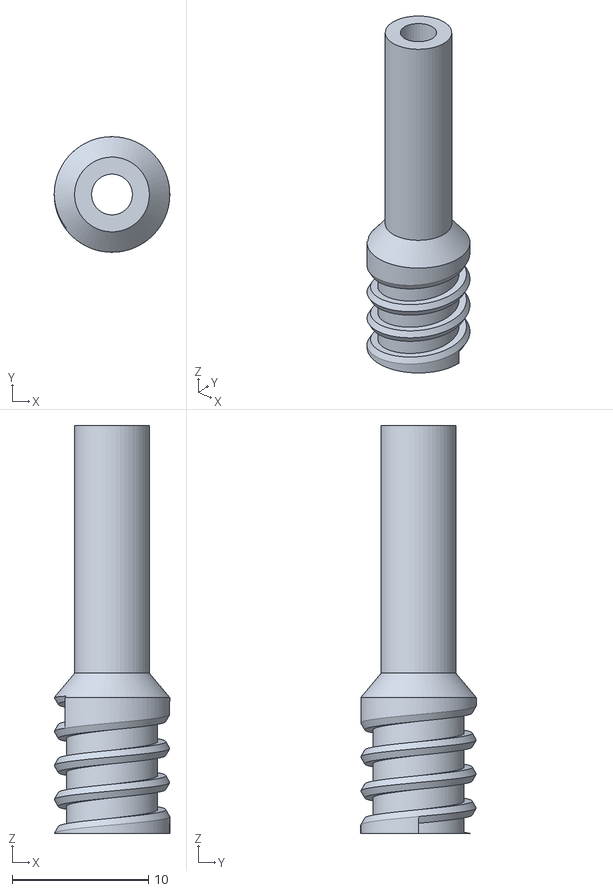
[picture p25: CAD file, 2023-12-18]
model/Body1.stl
8.50 x 8.50 x 30.0

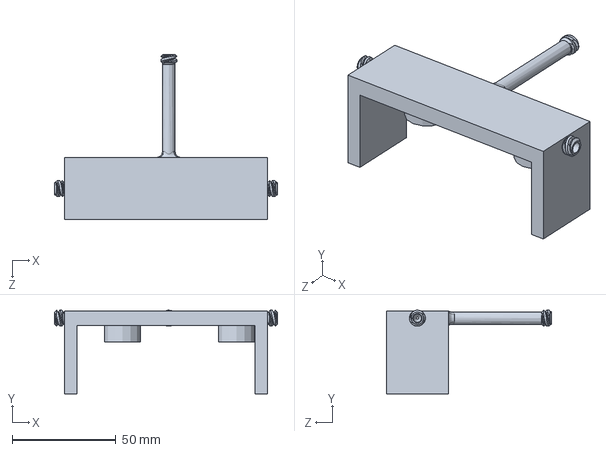
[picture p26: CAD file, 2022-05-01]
model/Ferrofluid Pump Electromagnets.SLDPRT
107.6 x 40.4 x 79.8 mm

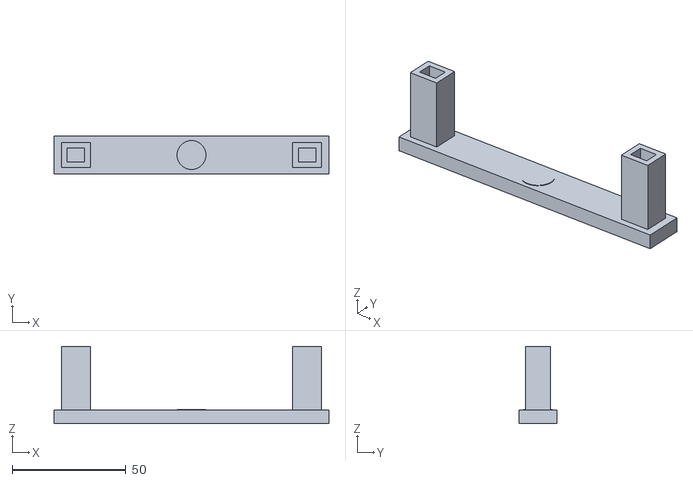
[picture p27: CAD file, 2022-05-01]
model/PumpConceptV0.2.stl
120.7 x 16.5 x 34.0

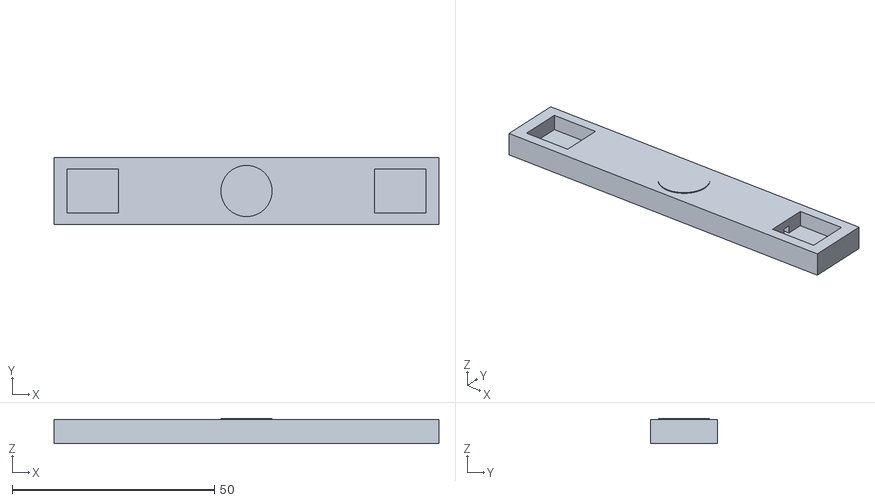
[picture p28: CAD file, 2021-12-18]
model/PumpConceptV0.1.stl
95.2 x 16.5 x 6.20

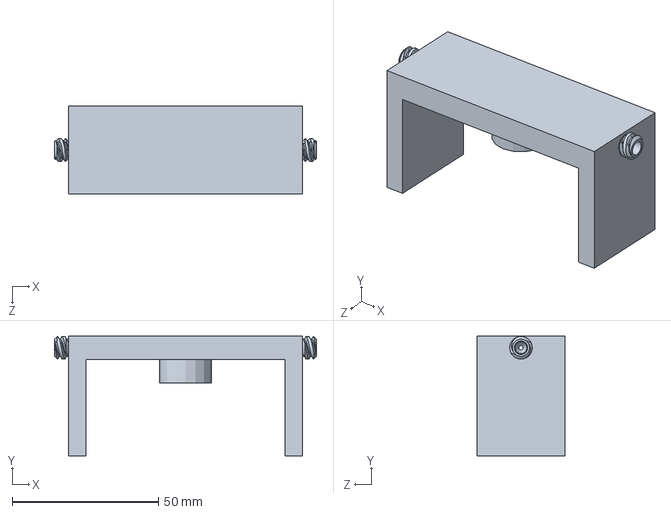
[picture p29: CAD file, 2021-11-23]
model/FerrofluidModel.SLDPRT
89.6 x 41.0 x 30.0 mm

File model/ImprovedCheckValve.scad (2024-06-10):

// Copyright Robert L. Read, 2022
// Released under CERN Strong-reciprocal Open Hardware License

// This is an attempt to make a new parametrized experimental apparatus
// for teting our ferrofluid check valve. It will be similar to the system
// that Veronica design in SolidWorks, but will use the improved, 360 degree design


// Thanks to  Mike Thompson for ths CC Attribution-NonCommercial-SA 3.0 set of threaded tools
// include <Nut_Job_v2.scad>;

$fn = 40;


SlabHeight = 5;
HighChamberHeight = 15;
AirGapChamberHeight = 8;
ChamberRadius = 35;
// The idea of the Constrained Chamber Radius is to have a diameter of 0.33 inches.
ConstrainedChamberRadius = 0.4* 25.4 / 2.0;
SlabLength = ChamberRadius*5.5;
SlabWidth = ChamberRadius*2.5;
ChannelWidth = 1.0;
ChannelWallWidth = 2.0;
PlaneThickness = 2.0;
MagnetHeight = 50;
ww = 1.5; // This is the wall width, assumed to be sturdy enough

BasicRailWidth = 2;
MagnetWidth = 12.8;


LuerPosition = SlabLength/2 - 5;
// LockRingHeight = 15;
LockRingHeight = 20;

PI = 3.14152;
GapHeight = 3.0;
Thickness = 1.0;

// ptype = "valve";
// ptype = "interior";
// ptype = "valveWithRails";//
// ptype = "constrainedValve";
// ptype = "airgapchamber";
ptype = "highchamber";
 module regular_polygon(order = 4, r=1){
     angles=[ for (i = [0:order-1]) i*(360/order) ];
     coords=[ for (th=angles) [r*cos(th), r*sin(th)] ];
     polygon(coords);
 }
 
 
 // Replicate a shape at a given radius and repeat with
 // rotation to create order number of objects
 module magnetChamber() {
     circle(CircleRadius);
 }
 
 module connectors(r, order=7) {
     difference() {
         circle(r*1.1);
         circle(r*0.8);
     }
//     color("gray")
     rotate(1.5 * 360 / order) 
        translate([r*1.5,0,0]) 
     square([2*a,a],center=true);
          color("gray")
     rotate(5.5 * 360 / order) 
        translate([r*1.5,0,0]) 
     square([2*a,a],center=true);
        
//    color("red") 
     translate([0.85*a,r+1.5*a,0])
     rotate([0,0,90])
      square([2*a,a],center=true);
     
//         color("red") 
     translate([0.85*a,-(r+1.5*a),0])
     rotate([0,0,90])
      square([2*a,a],center=true);
 }
module recoveryInterior(cr) {
    thickness = PlaneThickness*0.7;
    linear_extrude(height=thickness,center=true)
    union() {
        translate([cr*2.0,0])
        square([cr,cr],center=true); 
        crh = cr / 2;
        d = crh*3;
        points = [[d,crh], [d,-crh], [d-cr/3,0]];
        polygon(points);
    }
}
 module interior(cr) {
    thickness = PlaneThickness*0.7;
    union() {
        // First, we put in a rectangle that spans the whole thing
        linear_extrude(height=thickness,center=true)
        square([SlabLength*1.5,thickness],center=true);
        
        linear_extrude(height=thickness,center=true)
        difference() {
            circle(cr);
            union() {
                injectionWidth = PlaneThickness * 2;
 //               f = 0.2;
                f = 0.3;
                translate([-SlabLength/2,PlaneThickness* f,0])
                square([SlabLength,ChannelWidth*2],center=true);
                translate([-SlabLength/2,-PlaneThickness * f,0])
                square([SlabLength,ChannelWidth*2],center=true);
            }
        }
        // Now we adde the "recovery chambers"
        recoveryInterior(ChamberRadius);
        rotate([0,0,180])
        recoveryInterior(ChamberRadius);
    }
 }
 
 module luer() {
 //import("Body1.stl", convexity=3);
     myBarbJustForThis();
 }

module slab(r,cr) {
    l = r*4;
 //   color("red",0.2)
    linear_extrude(height = SlabHeight, center = true, convexity = 10, twist = 0)
    union() {
        circle(cr+5);
        square([5*r+10,r+5],center=true); 
    }
}

//module slabWithHighChamber(r,cr) {
//    l = r*4;
//    color("Green",1.0)
//    linear_extrude(height = HighChamberHeight, center = true, convexity = 10, twist = 0)
//    union() {
//        circle(cr+5);
//        square([5*r+10,r+5],center=true); 
//    }
//}

module basicRing(r) {
    w = 2;
    rotate([0,90,0])
    difference() {
        cylinder(LockRingHeight,r+w,r+w,center=true);
        cylinder(LockRingHeight+10,r,r,center=true);
    }
}
module basicRail(r) {
    w = BasicRailWidth;
    translate([0,0,0])
    cube([SlabWidth,w,LockRingHeight],center=true);
}

module lockRings() {
    // This should be the diameter of the permanent magnets used in the locks
    lockRadius =  MagnetWidth / 2;
    rotate([0,90,0])
    basicRing(lockRadius); 
}
module lockRails() {
    // This should be the diameter of the permanent magnets used in the locks
    r = (MagnetWidth / 2) + (BasicRailWidth/2);
    translate([0,r,0])   
    basicRail(r);  
    translate([0,-r,0])   
    basicRail(r);    
}

module addStands() {
    StandHeight = 2*25.4;
    translate([SlabLength/2+0,-SlabWidth/2,0])
    rotate([0,0,90])
    difference() {
        cube([SlabWidth,SlabHeight,SlabWidth]);
        translate([SlabWidth/4,-3,SlabWidth/3])
        cube([SlabWidth/2,SlabHeight*2,SlabWidth]);
    }
    translate([-SlabLength/2+SlabHeight,-SlabWidth/2,0])
    rotate([0,0,90])
    difference() {
        cube([SlabWidth,SlabHeight,SlabWidth]); 
        translate([SlabWidth/4,-3,SlabWidth/3])
        cube([SlabWidth/2,SlabHeight*2,SlabWidth]);
    }  
}

module completeValve() {
    c = ChamberRadius/2;
    union() {
        translate([LuerPosition,0,0]) rotate([0,270,0]) luer();
        translate([-LuerPosition,0,0]) rotate([0,90,0]) luer();
        difference() {
          union() {
             slab(ChamberRadius,ChamberRadius);
             lockRings();
          }
         interior(hamberRadius);
       }
       // now we add a "blocking bar"
       translate([ChamberRadius*2.0,0])
       cube([2,c,SlabHeight],center=true);
       translate([-ChamberRadius*2.0,0])
       cube([2,c,SlabHeight],center=true);
    } 
}

module valveWithRails(r,cr) {
    c = r/2;
    union() {
        translate([LuerPosition,0,0]) rotate([0,270,0]) luer();
        translate([-LuerPosition,0,0]) rotate([0,90,0]) luer();
        difference() {
          union() {
             slab(r,cr);
             lockRails();
          }
         interior(cr);
       }
       // now we add a "blocking bar"
       translate([r*2.0,0])
       cube([2,c,SlabHeight],center=true);
       translate([-r*2.0,0])
       cube([2,c,SlabHeight],center=true);
    } 
}
 
module chamberDrum(cr,chamberHeight) {
    rotate([0,0,180])
    translate([0,0,-(ChannelWidth+ChannelWallWidth)/2])
    difference() {
        union() {
            color("blue",0.6)
//            translate([0,0,-ChannelWallWidth/2])
            translate([0,0,-0.5])
            difference() { 
                linear_extrude(chamberHeight, twist = 0)            
                 circle(cr+ww);
                translate([0,0,ChannelWallWidth])   
                linear_extrude(chamberHeight-2*ChannelWallWidth, twist = 0)            
                circle(cr);
            }
            // Now we add the channel.
            translate([cr,0,(ChannelWidth+ChannelWallWidth)/2])
            difference() {
                cube([cr*2,ChannelWidth+ChannelWallWidth,ChannelWidth+ChannelWallWidth],center=true);
                cube([cr*3,ChannelWidth,ChannelWidth],center=true);
            }
     }
     translate([cr,0,(ChannelWidth+ChannelWallWidth)/2])
     cube([cr*6,ChannelWidth,ChannelWidth],center=true);
    }
    
 
}

module valveWithHighChamber(r,chamberHeight) {
    c = r/2;
    cr = c;
//   translate([0,0,0])
//   interior(cr);
    
    difference() {
    union() {
        translate([LuerPosition,0,0]) rotate([0,270,0]) luer();
        translate([-LuerPosition,0,0]) rotate([0,90,0]) luer();
        chamberDrum(cr,chamberHeight);
        difference() {
            union() {
                difference() {
                    union() {
                        slab(r,cr); 
                        lockRails();
                    }
                    translate([0,0,-PlaneThickness/2])
                    linear_extrude(chamberHeight-2*ChannelWallWidth, twist = 0)            
                    circle(cr+ww);         
                }
            };      
        }
    }
    interior(cr);
    }  
   
   // now we add a "blocking bar"
//    translate([0,30,0])
       translate([r*2.0,0])
       cube([2,c,SlabHeight],center=true);
 //   translate([0,30,0])
       translate([-r*2.0,0])
       cube([2,c,SlabHeight],center=true); 
    // Now cut this:
    
   difference() {
      q = 0.8;
      m = 0.7;
      color("white", 1.0)
      translate([cr+-m,0,chamberHeight/2-4])
      rotate([0,90,0])
      difference() {
        cube([chamberHeight-3,ChannelWidth+ChannelWallWidth+q,ChannelWidth+ChannelWallWidth+q],center=true);
        cube([chamberHeight*2,ChannelWidth+q,ChannelWidth+q],center=true);
     }
     f = 1.2;
     g = 0.4;
     translate([cr+2,0,0])    
     cube([ChannelWidth*f+4,ChannelWidth*f+g,ChannelWidth*f+g],center=true);
   }
}
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

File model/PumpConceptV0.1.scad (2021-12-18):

//
//    PumpConcept - V 0.1
//    Copyright (C) 2021  Robert L. Read
//
//    This program is free software: you can redistribute it and/or modify
//    it under the terms of the GNU General Public License as published by
//    the Free Software Foundation, either version 3 of the License, or
//    (at your option) any later version.
//
//    This program is distributed in the hope that it will be useful,
//    but WITHOUT ANY WARRANTY; without even the implied warranty of
//    MERCHANTABILITY or FITNESS FOR A PARTICULAR PURPOSE.  See the
//    GNU General Public License for more details.
//
//    You should have received a copy of the GNU General Public License
//    along with this program.  If not, see <https://www.gnu.org/licenses/>.

// This is an experimental attempt to design a ferrofluid pump with no moving parts.abs
// I will attempt to make this as a linear extrusion of the chamber space, and then
// subtract that from the solid shape.abs
// I am attempting to build the simplest apparatus that can be used to test the 
// hypothesis that oscillating the magnitude (not direction) of the field can 
// create flow.

CircularMagnetDiameter = 12.7; // We use a half-inch magnet
CMD = CircularMagnetDiameter;
ChamberHeightZ = 2.0; // We will make a 2.0 mm high chamber
WellHeightZ = 4.0;
EqTriHeight = sqrt(3)/2;
SideLength = sqrt(3) * CMD;
InscribedRadius = sqrt(3)/6;
ChamberWidth = 1.0 * EqTriHeight * CMD;
ChamberLength = 1.0 * CMD;
ChannelLength = 5 * CMD; // we want a nice long chamber to be able to see the
// pumping effect visually.
ChannelWidth = 2.0;

TriangularLength = 0.7 * CMD;
ThickChamberLength = CMD / 2;

// Now I will union together two triangles, a rectangle, and long
// channel for the purpose of building this.

 module regular_polygon(order = 4, r=1){
     angles=[ for (i = [0:order-1]) i*(360/order) ];
     coords=[ for (th=angles) [r*cos(th), r*sin(th)] ];
     polygon(coords);
 }

module chamber() {
    union() {
        translate([0,0,WellHeightZ - ChamberHeightZ/2])
        linear_extrude(height = WellHeightZ*2, center = true, slices = 20, scale = 1.0, $fn = 16)
        union() {
            translate([-ChamberLength/2+-(ChannelLength/2)+.1,0,0])
            square([ChamberLength,ChamberWidth],true);
        
            translate([+ChamberLength/2+(ChannelLength/2)-.1,0,0])
            square([ChamberLength,ChamberWidth],true);
        }
        linear_extrude(height = ChamberHeightZ, center = true, slices = 20, scale = 1.0, $fn = 16)
        union() {
        translate([0,0,0])
        square([ChannelLength,ChannelWidth],true);
        translate([0,0,0])
        color("red")
        translate([-(ChamberLength/2 + SideLength*EqTriHeight/6),0,0])
            square([ChamberLength,ChamberWidth],true);
            
        regular_polygon(order = 3, r=CMD/2);
            
        %color("blue")
        translate([-(3*ChamberLength/2 + 0*EqTriHeight * SideLength / 3),0,0])
        rotate([0,0,180])
        regular_polygon(order = 3, r=CMD/2);
        }
    }
}

module referenceCircle() {
    circle(r = CMD/2);
}

module holdingSlab() {
    translate([0,0,0])
    cube([ChannelLength+ChamberLength*2.5,ChamberWidth*1.5,ChamberHeightZ*3],true);
}

union() {
    color("red")
    translate([0,0,ChamberHeightZ*3/2])
    linear_extrude(height = 0.4, center = true, slices = 20, scale = 1.0, $fn = 32)
    referenceCircle();
    difference() {
        holdingSlab();
        chamber();
    }
}

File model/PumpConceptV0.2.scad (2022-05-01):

//
//    PumpConcept - V 0.1
//    Copyright (C) 2021  Robert L. Read
//
//    This program is free software: you can redistribute it and/or modify
//    it under the terms of the GNU General Public License as published by
//    the Free Software Foundation, either version 3 of the License, or
//    (at your option) any later version.
//
//    This program is distributed in the hope that it will be useful,
//    but WITHOUT ANY WARRANTY; without even the implied warranty of
//    MERCHANTABILITY or FITNESS FOR A PARTICULAR PURPOSE.  See the
//    GNU General Public License for more details.
//
//    You should have received a copy of the GNU General Public License
//    along with this program.  If not, see <https://www.gnu.org/licenses/>.

// This is an experimental attempt to design a ferrofluid pump with no moving parts.abs
// I will attempt to make this as a linear extrusion of the chamber space, and then
// subtract that from the solid shape.abs
// I am attempting to build the simplest apparatus that can be used to test the 
// hypothesis that oscillating the magnitude (not direction) of the field can 
// create flow.

CircularMagnetDiameter = 12.7; // We use a half-inch magnet
CMD = CircularMagnetDiameter;
ChamberHeightZ = 2.0; // We will make a 2.0 mm high chamber
WellHeightZ = 4.0;
EqTriHeight = sqrt(3)/2;
SideLength = sqrt(3) * CMD;
InscribedRadius = sqrt(3)/6;
ChamberWidth = 1.0 * EqTriHeight * CMD;
ChamberLength = 1.0 * CMD;
ChannelLength = 7 * CMD; // we want a nice long chamber to be able to see the
// pumping effect visually.
ChannelWidth = 2.0;

TriangularLength = 0.7 * CMD;
ThickChamberLength = CMD / 2;

// Now I will union together two triangles, a rectangle, and long
// channel for the purpose of building this.

 module regular_polygon(order = 4, r=1){
     angles=[ for (i = [0:order-1]) i*(360/order) ];
     coords=[ for (th=angles) [r*cos(th), r*sin(th)] ];
     polygon(coords);
 }

module chamber() {
    union() {
        translate([0,0,WellHeightZ - ChamberHeightZ/2])
        linear_extrude(height = WellHeightZ*2, center = true, slices = 20, scale = 1.0, $fn = 16)
        union() {
            translate([-ChamberLength/2+-(ChannelLength/2)+.1,0,0])
            square([ChamberLength,ChamberWidth],true);
        
            translate([+ChamberLength/2+(ChannelLength/2)-.1,0,0])
            square([ChamberLength,ChamberWidth],true);
        }
        linear_extrude(height = ChamberHeightZ, center = true, slices = 20, scale = 1.0, $fn = 16)
        union() {
        translate([0,0,0])
        square([ChannelLength,ChannelWidth],true);
        translate([0,0,0])
        color("red")
        translate([-(ChamberLength/2 + SideLength*EqTriHeight/6),0,0])
            square([ChamberLength,ChamberWidth],true);
            
        regular_polygon(order = 3, r=CMD/2);
            
        color("blue")
        translate([-(3*ChamberLength/2 + 0*EqTriHeight * SideLength / 3),0,0])
        rotate([0,0,180])
        regular_polygon(order = 3, r=CMD/2);
        }
    }
}

module twoColumns() {
          columnThickness = 5;
difference() {
  union() {
      f = 8;

      color("red")
     translate([0,0,WellHeightZ*f/2 - ChamberHeightZ/2])
     linear_extrude(height = WellHeightZ*f, center = true, slices = 20, scale = 1.0, $fn = 16)
     union() {
            translate([-ChamberLength/2+-(ChannelLength/2)+.1,0,0])
            difference() {
                square([ChamberLength,ChamberWidth],true);
                square([ChamberLength-columnThickness,ChamberWidth-columnThickness],true);
            }
        
            translate([+ChamberLength/2+(ChannelLength/2)-.1,0,0])
            difference() {
                square([ChamberLength,ChamberWidth],true);
                square([ChamberLength-columnThickness,ChamberWidth-columnThickness],true);
           }
     }
  }
  // here we subtract out the long channel
   linear_extrude(height = ChamberHeightZ, center = true, slices = 20, scale = 1.0, $fn = 16)
   translate([0,0,0])
   square([ChannelLength+columnThickness*2 +.1,ChannelWidth],true);
  }
}

module referenceCircle() {
    circle(r = CMD/2);
}

module holdingSlab() {
    translate([0,0,0])
    cube([ChannelLength+ChamberLength*2.5,ChamberWidth*1.5,ChamberHeightZ*3],true);
}

union() {
    color("red")
    translate([0,0,ChamberHeightZ*3/2])
    linear_extrude(height = 0.4, center = true, slices = 20, scale = 1.0, $fn = 32)
    referenceCircle();

    difference() {
        holdingSlab();
        chamber();
    }  
    twoColumns();
}

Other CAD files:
model/FerrofluidModel.STL

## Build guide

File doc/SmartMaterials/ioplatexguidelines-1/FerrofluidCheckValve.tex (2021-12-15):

%%%%%%%%%%%%%%%%%%%%%%%%%%%%%%%%%%%%%%%%%%%%%%%%%%%%%%%%%%%%%%%%%%%%%%%%
%    INSTITUTE OF PHYSICS PUBLISHING                                   %
%                                                                      %
%   `Preparing an article for publication in an Institute of Physics   %
%    Publishing journal using LaTeX'                                   %
%                                                                      %
%    LaTeX source code `ioplau2e.tex' used to generate `author         %
%    guidelines', the documentation explaining and demonstrating use   %
%    of the Institute of Physics Publishing LaTeX preprint files       %
%    `iopart.cls, iopart12.clo and iopart10.clo'.                      %
%                                                                      %
%    `ioplau2e.tex' itself uses LaTeX with `iopart.cls'                %
%                                                                      %
%%%%%%%%%%%%%%%%%%%%%%%%%%%%%%%%%%
%
%
% First we have a character check
%
% ! exclamation mark    " double quote
% # hash                ` opening quote (grave)
% & ampersand           ' closing quote (acute)
% $ dollar              % percent
% ( open parenthesis    ) close paren.
% - hyphen              = equals sign
% | vertical bar        ~ tilde
% @ at sign             _ underscore
% { open curly brace    } close curly
% [ open square         ] close square bracket
% + plus sign           ; semi-colon
% * asterisk            : colon
% < open angle bracket  > close angle
% , comma               . full stop
% ? question mark       / forward slash
% \ backslash           ^ circumflex
%
% ABCDEFGHIJKLMNOPQRSTUVWXYZ
% abcdefghijklmnopqrstuvwxyz
% 1234567890
%
%%%%%%%%%%%%%%%%%%%%%%%%%%%%%%%%%%%%%%%%%%%%%%%%%%%%%%%%%%%%%%%%%%%
%
\documentclass[12pt]{iopart}
\newcommand{\gguide}{{\it Preparing graphics for IOP Publishing journals}}
%Uncomment next line if AMS fonts required
%\usepackage{iopams}
\usepackage{graphicx}
\usepackage{hyperref}   % to set up hyperlinks
\hypersetup{
	colorlinks=true,
	linkcolor=blue,
	citecolor=blue,
	urlcolor=blue,
}

\begin{document}

\note{A novel passive
ferrofluid check (one-way) valve}

% \title{A Novel Passive Ferrofluid One-way (Check) Valve}

%%% first author
\author{Veronica Stuckey$^1$
}
\address{$^1$Biomedical Engineer
}
\ead{stuckey002@gmail.com}
%%% second author
%%% remove the following entry for single author papers
%%% add more entries for additional authors
\author{Robert L. Read$^2$
}

\address{$^2$Public Invention, 1709 Norris Dr., Austin, TX, 78704,
}
\ead{read.robert@gmail.com}
\begin{abstract}

Small pumps and valves enable flow management in microfluidic systems.
A novel passive ferrofluid check valve is presented.
The valve consists of only a
unique channel-and-chamber geometry, ferrofluid, and a stationary
magnetic field.
The flow is determined only by the inlet and output pressure,
and the magnetic field is completely static.
The prototype valve and experimental setup are explained
and performance of the valves cracking and collapse pressure reported.
This initial design can be used for microfluid handling and lab-on-a-chip
applications.
\end{abstract}

%
% Uncomment for keywords
\vspace{2pc}
\noindent{\it Keywords}: ferrofluid, check valve, one-way valve

% Uncomment for Submitted to journal title message
\submitto{\SMS}
%
% Uncomment if a separate title page is required
%\maketitle
%
% For two-column output uncomment the next line and choose [10pt] rather than [12pt] in the \documentclass declaration
%\ioptwocol
%

%%%%%%%%%%%%%%%%%%%%%%%%%%%%%%%%%%%%%%%%%%%%%%%%%%%%%%%%%%%%%%%%%%%%%%
\section{Introduction}

Ferrofluid can be manipulated by electronically controlled magnetic
fields to exert force on fluids\cite{torres2014recent,kole2021engineering,ozbey2015modeling}.
This makes it possible to build pneumatic or hydraulic
devices, perhaps on very small scales,
such as a single chip\cite{yamahata2003ferrofluid,hatch2001ferrofluidic}, to
miniaturize fluid handling.
This has been proposed for biomedical purposes\cite{michelson2019novel}
that would use water or body fluids,
although this paper reports only on experiments done with air.
Miniature pumps and valves could be used to make a “lab on a chip” (LOC) or
even to heat or cool different chip areas.

A fundamental component of such
devices is the {\em check} or one-way valve.
Two check
valves on either side of a chamber whose volume can vary creates a
positive displacement pump.
A perfect check valve opens or
{\em cracks} with minimal pressure on the inlet side and sustains maximal
pressure on the outlet side before {\em collapse},
allowing fluid to flow in only one
direction. Following\cite{hartshorne2004ferrofluid} we call the maximum pressure
differential the valve can resist in the direction it is intended to
check or block (from outlet to inlet) the {\em sustainable} or {\em collapse} pressure.

This article is a brief report on an initial but functioning design of a
passive ferrofluid check valve (PFCV) that has no moving
parts except for the ferrofluid bolus itself, which is stationary
in normal operation.
By passive, the authors
mean a check valve that functions without changes to the magnetic
field affecting the bolus, whether that field is induced by a
permanent magnet or an electromagnet.
That is, the flow is determined
purely by the difference between the inlet port pressure and the
outlet port pressure.
To our knowledge, no passive
ferrofluid check valve has been previously reported, despite being an
active area of research and despite such a valve having
significant advantages for operation and especially
fabrication over valves with moving parts.

%%%%%%%%%%%%%%%%%%%%%%%%%%%%%%%%%%%%%%%%%%%%%%%%%%%%%%%%%%%%%%%%%%%%%%
\section{Related Research}

A number of papers report on ferrofluid pumps, focusing in particular
on micropump and lab-on-a-chip applications\cite{ozbey2015modeling,hsu2018biocompatible}.
Many of these papers use
a version of mechanical valve not based on passive
ferrofluid, even though they move a ferrofluid bolus
with a magnetic field.
For example,
a corrugated silicone micro valve\cite{yamahata2003ferrofluid,yamahata2005plastic}
has been reported.
Other researchers use active valves, which require synchronization with
the ferrofluid plug to form a pump,
such as \cite{menz2000fluidic}, which
describes an active {\em T-Valve} with a moving ferrofluid plug, and
\cite{ando2009ferrofluidic} describes a complete fluid pump with valves
that use
active control of a ferrofluid bolus.
At least two additional kinds of active valves, a {\em well valve} and
{\em Y-valve}, have
been described\cite{hartshorne2004ferrofluid}.
Active control is possible because the
action of the plunger or bolus may be synchronized with the opening and closing
of the valves.
Nonetheless a passive valve would be simpler and less
expensive, and would not require knowledge of the timing of the
plunger.

An interesting functional micropump in which the
moving ferrofluid bolus merges with a fixed ferrofluid valve and then
separates on each pumping cycle has been described\cite{hatch2001ferrofluidic},
but is not a one-way valve.

A passive ferrofluid two-way valve with tunable
opening and closing pressure based on magnetic
field strength\cite{paschalis2013novel} has been tested,
but could not be passively used to make a pump.

This paper has not studied the closing pressure of the PFCV, but reports on
the opening (or cracking) pressure (for flow from inlet to outlet) and
sustainable (or collapse) pressure
when the outlet pressure is higher than the inlet side.

\section{Passive Ferrofluid Check Valve (PFCV) Design}
%%%%%%%%%%%%%%%% begin figure %%%%%%%%%%%%%%%%%%%
%%% 3.34in is the maximum width you can have for a figure
\begin{figure}
\centerline{}
\caption{The passive ferrofluid check valve components}
\label{fig_components}
\end{figure}
%%%%%%%%%%%%%%%% end figure %%%%%%%%%%%%%%%%%%%

The PFCV depicted in Fig.~\ref{fig_components} is a simple asymmetric volume
centered in a magnetic field
which holds a ferrofluid bolus in place.
In the center of a radially symmetric magnetic field
a narrow channel meets a larger open chamber at a right angle.
The ferrofluid bolus is large enough that at rest in the field it
forms a semi-circle in the open chamber. The narrow channel is
longer than the radius of the bolus at rest.
The broad chamber is the outlet side of the valve.
The narrow chamber opens onto a recovery chamber on the inlet
side of the valve.
This design allows the bolus to be recovered from the recovery
chamber when the pressure is equalized if the outlet pressure is
raised above the collapse pressure, driving the bolus away
from the magnetic field.
The PFCV does not resist pressure as well  as a
valve of the same size
made out of moving, solid parts.
That is, the sustainable
pressure it can resist on the outlet side before failing is relatively
low, and pressure required to crack it open and allow flow is
relatively high.
However, it may operate reliably within a range of
known pressures, and thus be sufficient to build a
pump-on-a-chip.
Furthermore, the PFCV reported here is a preliminary design which
can probably be significantly improved.
The authors found the
existence of the PFCV worth sharing immediately.

\section{Method}

The valve depicted Fig.~\ref{fig_components}
was designed using Solidworks 2016.
It is freely licensed via the CERN OHL Strong Reciprocal License\cite{stuckey2021,stuckey2021stl}.
The model consists of a 15mm long, 2mm wide channel, a large outlet
chamber, a recovery chamber,
two female luers, a magnet holder ring and two legs to provide room
for the magnet.  All volumes are 2mm high.
The 3D shape
of the chambers can be thought as a 2mm high extrusion of a 2D shape.
Viewed from the top, one end opens up to a recovery
chamber of circular profile 30mm in diameter and the other
an outlet chamber with a flat wall.
A magnet holder ring 12.7mm inner diameter (1/2'') was created centered on the channel-chamber
junction, below where the bolus is placed, to hold a permanent magnet in place
at the center of the valve. When two magnets are used, the magnet on
top naturally stays in the same position due to attraction to the magnet below.
On the inlet side of the channel
opens into a recovery chamber shaped to allow the ferrofluid to be
passively drawn back into the channel by the magnetic field after a
collapse of the bolus.
The model was printed on a Projet MJP 2500 (3D
Systems, Rock Hill, SC), using Visijet M2G-CL and VisiJet M2 SUP as
material and support respectively (3D Systems, Rock Hill, SC). Support
material was removed by using an EasyClean system (3D Systems, Rock
Hill, SC) and Dawn dish soap (Procter \& Gamble, Cincinnati, OH) to
remove residuals.

%%%%%%%%%%%%%%%% begin figure %%%%%%%%%%%%%%%%%%%
%%% 3.34in is the maximum width you can have for a figure
\begin{figure}
\centerline{}
\caption{Equipment set up}
\label{fig_equipment}
\end{figure}
%%%%%%%%%%%%%%%% end figure %%%%%%%%%%%%%%%%%%%

As shown in Fig.~\ref{fig_equipment} and in our demonstration video\cite{stuckey2021video},
a basixCOMPAK 30atm pressurizing syringe (Merit Medical, South Jordan,
UT) is connected to the model via a two-way stopcock (Qosina,
Ronkonkoma, NY), tubing (Natvar, City of Industry, CA), and male
(Injectech, Fort Collins, CO) and female luer (Qosina, Ronkonkoma,
NY), allowing integration of a manometer (General Tools, Secaucus, NJ)
to measure pressure. A 12.7mm x 25.4mm (1/2” x 1”)
cylindrical neodymium magnet (Apex
Magnets, Petersburg, WV) with a pull force of 14.6 kg (32.24 pounds)
was placed inside the magnet channel by means
of a tight fit and 0.2 mL of ferrofluid (Apex Magnets, Petersburg, WV)
was injected into the model using a 3mL syringe (BH Supplies, Jackson,
NJ).

To obtain values, pressure was applied through the pressurizing
syringe, as demonstrated in a video \cite{stuckey2021video}.
Pressure was first applied from the outlet side of the model.
The maximum pressure difference from the outlet side that the
valve can withstand before collapsing, will be referred to as the
sustainable pressure or {\em collapse} pressure.
Pressure applied from the inlet needed to
initiate flow will be referred to as the {\em cracking} pressure.

The cracking pressure was first measured by increasing the pressure
difference on the inlet side until flow is initiated (at which point
the valve is ``open'' and
pushing the syringe plunger faster simply increases flow without
increasing the pressure.) Then the
collapse pressure was measured by increasing the pressure
difference on the outlet side. At pressures below the sustainable
pressure, the valve holds pressure well with no observable leaks of
air in the short time (a few minutes) of our experiment. When the
sustainable pressure is exceeded, the bolus explodes violently into
the recovery chamber. When the pressure difference is equalized, the
bolus may passively recover into the central position, or it may need
to be actively “combed” with a magnet back into the central position.

The procedure was performed first with one magnet, named the “Single
Magnet” configuration, placed below the channel-chamber connection.
The “Dual Magnet” configuration was performed with the magnet in the
same position as the Single Magnet case in the same position, but with
a second magnet of the same kind placed vertically on top of the model,
arranged to be strongly attracted to the lower magnet.

\section{Results}
The final pressures obtained demonstrate a clear difference between
the inlet cracking pressure and outlet sustainable pressure, creating
an effective passive check valve.

\lineup

%%%%%%%%%%%%%%% begin table   %%%%%%%%%%%%%%%%%%%%%%%%%%
\begin{table}[t]
\footnotesize
\caption{\label{table_ASME}Result pressures}
\begin{indented}
\item[]
\begin{tabular}{@{}lllll}
% \begin{tabular}{|p{1.0in} |p{1.0in} |p{1.0in} |p{0.7in} |p{1.0in} |}
\br
 &
Cracking  &
Collapse &
Pressure &
Approx. Ratio: \\
Magnet &
Pressure &
Pressure  &
Difference &
Cracking to \\
configuration &
kPa  (mmHg) &
kPa  (mmHg) &
kPa  (mmHg) &
Collapse Pr. \\
\mr
Single &
1.1 \0(8) &
\05.5 (41) &
4.4 (33) &
1:5 \\
\br
Dual &
8.5 (64) &
17.5 (131)&
8.9 (67)&
1:2 \\
\br
\end{tabular}
\end{indented}
\end{table}
%%%%%%%%%%%%%%%% end table %%%%%%%%%%%%%%%%%%%

The ferrofluid had observable differences in behavior between the two
configurations.  After the pressure equalized
following a collapse of the bolus due to
exceeding the sustainable pressure, the single magnet
configuration often repaired itself by drawing the fluid back
into a centered bolus passively.
After a collapse with two magnets, fluid further from the bolus
remained stationary while the fluid closer was pulled back to the
center. Following the removal of the top magnet, the stationary fluid
then began to return to the bolus. This is consistent with the
localization of the magnetic field between two magnets, and the
weakening of the magnetic field further from the channel-chamber
juncture in the dual magnet configuration.

Although the dual magnet configuration demonstrated a larger absolute
pressure difference due to magnetic field strength between the
cracking and the collapse pressure, the single magnet configuration
granted a larger ratio of collapse pressure to cracking
pressure due to the much lower cracking pressure.
The authors conjecture that the low cracking pressure may have
been not only to the weaker magnetic field, but the weakening at the
top of the 2mm high channel, which was further away from the magnet
in the single magnet configuration.

\section{Conclusions}

This paper demonstrates an apparently novel passive ferrofluid one-way
valve or check valve (PFCV). This valve is completely passive in that
it depends entirely on the pressure at the inlet port and the outlet
port. The valve has no moving parts (except for the ferrofluid, which
is almost stationary), and a remarkably simple design, consisting of
nothing but a channel, an inlet chamber, and outlet chamber,
and a bolus of ferrofluid in a
static magnetic field.

Although no effort has been made to optimize the design, the pressure
difference between the cracking pressure and the sustainable back
pressure appear great enough to make an effective micropump. The
performance of this one-way valve may improve with additional design
effort; the authors sought to publish this result as soon as it was
observed.  Obvious future research possibilities are:
\begin{enumerate}
\item  To improve the
performance by varying the geometry of the passive design or shape and
strength of the magnetic field.
\item Utilizing this design to make a micro-pump
similar to earlier micro-pumps but with this simpler check valve
design.
\item To provide an explanatory and predictive theory of operation,
for example based on magnetic field strength as per \cite{ando2009ferrofluidic}.
\item Studying the ability of the valve to recover after
  a collapse automatically when high outlet pressure is removed,
  which would increase robustness in some applications.
\end{enumerate}

\section{Acknowledgements}

Robert L. Read designed the PFVC. Veronica Stuckey designed, printed,
and tested the model. Both authors contributed to the text of this paper.

\section*{References}

\bibliographystyle{unsrt}
% Here's where you specify the bibliography database file.
% The full file name of the bibliography database for this
% article is asme2e.bib. The name for your database is up
% to you.
\bibliography{ffcv}

\end{document}

‘This is the version of the article before peer review or editing, as submitted by an author to [INSERT NAME OF JOURNAL].  IOP Publishing Ltd is not responsible for any errors or omissions in this version of the manuscript or any version derived from it.  The Version of Record is available online at [INSERT DOI]’

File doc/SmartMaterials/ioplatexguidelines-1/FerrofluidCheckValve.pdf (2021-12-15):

Note

## A novel passive ferrofluid check (one-way) valve

Veronica Stuckey¹

1Biomedical Engineer

E-mail: stuckey002@gmail.com

Robert L. Read²

2Public Invention, 1709 Norris Dr., Austin, TX, 78704,

E-mail: read.robert@gmail.com

Abstract.
Small pumps and valves enable flow management in microfluidic systems. A novel passive ferrofluid check valve is presented. The valve consists of only a unique channel-and-chamber geometry, ferrofluid, and a stationary magnetic field. The flow is determined only by the inlet and output pressure, and the magnetic field is completely static. The prototype valve and experimental setup are explained and performance of the valves cracking and collapse pressure reported. This initial design can be used for microfluid handling and lab-on-a-chip applications.

Keywords: ferrofluid, check valve, one-way valve

Submitted to: Smart Mater. Struct.

### 1. Introduction

Ferrofluid can be manipulated by electronically controlled magnetic fields to exert force on fluids[1, 2, 3]. This makes it possible to build pneumatic or hydraulic devices, perhaps on very small scales, such as a single chip[4, 5], to miniaturize fluid handling. This has been proposed for biomedical purposes[6] that would use water or body fluids, although this paper reports only on experiments done with air. Miniature pumps and valves could be used to make a “lab on a chip” (LOC) or even to heat or cool different chip areas. A fundamental component of such devices is the check or one-way valve. Two check valves on either side of a chamber whose volume can vary creates a positive displacement pump. A perfect check valve opens or cracks with minimal pressure on the inlet side and sustains maximal pressure on the outlet side before collapse, allowing fluid to flow in only one direction. Following[7] we call the maximum pressure differential the valve

A novel passive ferrofluid check (one-way) valve | 2

can resist in the direction it is intended to check or block (from outlet to inlet) the sustainable or collapse pressure.
This article is a brief report on an initial but functioning design of a passive ferrofluid check valve (PFCV) that has no moving parts except for the ferrofluid bolus itself, which is stationary in normal operation. By passive, the authors mean a check valve that functions without changes to the magnetic field affecting the bolus, whether that field is induced by a permanent magnet or an electromagnet. That is, the flow is determined purely by the difference between the inlet port pressure and the outlet port pressure. To our knowledge, no passive ferrofluid check valve has been previously reported, despite being an active area of research and despite such a valve having significant advantages for operation and especially fabrication over valves with moving parts.

### 2. Related Research

A number of papers report on ferrofluid pumps, focusing in particular on micropump and lab-on-a-chip applications[3, 8]. Many of these papers use a version of mechanical valve not based on passive ferrofluid, even though they move a ferrofluid bolus with a magnetic field. For example, a corrugated silicone micro valve[4, 9] has been reported. Other researchers use active valves, which require synchronization with the ferrofluid plug to form a pump, such as [10], which describes an active T-Valve with a moving ferrofluid plug, and [11] describes a complete fluid pump with valves that use active control of a ferrofluid bolus. At least two additional kinds of active valves, a well valve and Y-valve, have been described[7]. Active control is possible because the action of the plunger or bolus may be synchronized with the opening and closing of the valves. Nonetheless a passive valve would be simpler and less expensive, and would not require knowledge of the timing of the plunger.
An interesting functional micropump in which the moving ferrofluid bolus merges with a fixed ferrofluid valve and then separates on each pumping cycle has been described[5], but is not a one-way valve.
A passive ferrofluid two-way valve with tunable opening and closing pressure based on magnetic field strength[12] has been tested, but could not be passively used to make a pump.
This paper has not studied the closing pressure of the PFCV, but reports on the opening (or cracking) pressure (for flow from inlet to outlet) and sustainable (or collapse) pressure when the outlet pressure is higher than the inlet side.

### 3. Passive Ferrofluid Check Valve (PFCV) Design

The PFCV depicted in Fig. 1 is a simple asymmetric volume centered in a magnetic field which holds a ferrofluid bolus in place. In the center of a radially symmetric magnetic field a narrow channel meets a larger open chamber at a right angle. The ferrofluid

A novel passive ferrofluid check (one-way) valve | 3

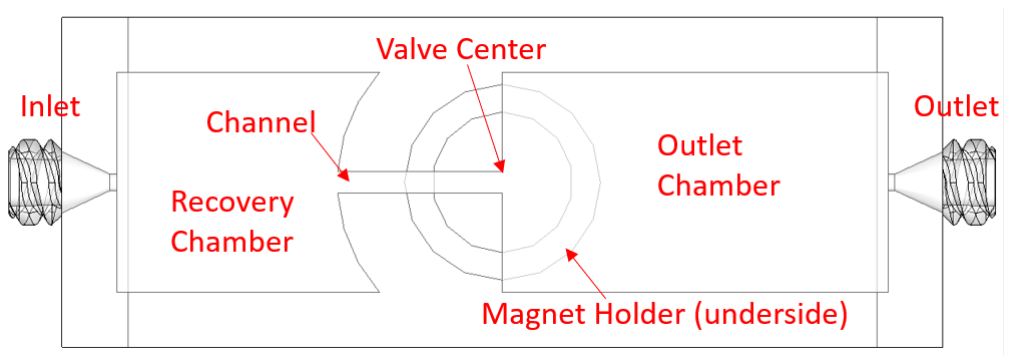
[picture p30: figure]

Figure 1. The passive ferrofluid check valve components

bolus is large enough that at rest in the field it forms a semi-circle in the open chamber. The narrow channel is longer than the radius of the bolus at rest. The broad chamber is the outlet side of the valve. The narrow chamber opens onto a recovery chamber on the inlet side of the valve. This design allows the bolus to be recovered from the recovery chamber when the pressure is equalized if the outlet pressure is raised above the collapse pressure, driving the bolus away from the magnetic field. The PFCV does not resist pressure as well as a valve of the same size made out of moving, solid parts. That is, the sustainable pressure it can resist on the outlet side before failing is relatively low, and pressure required to crack it open and allow flow is relatively high. However, it may operate reliably within a range of known pressures, and thus be sufficient to build a pump-on-a-chip. Furthermore, the PFCV reported here is a preliminary design which can probably be significantly improved. The authors found the existence of the PFCV worth sharing immediately.

### 4. Method

The valve depicted Fig. 1 was designed using Solidworks 2016. It is freely licensed via the CERN OHL Strong Reciprocal License[13, 14]. The model consists of a 15mm long, 2mm wide channel, a large outlet chamber, a recovery chamber, two female luers, a magnet holder ring and two legs to provide room for the magnet. All volumes are 2mm high. The 3D shape of the chambers can be thought as a 2mm high extrusion of a 2D shape. Viewed from the top, one end opens up to a recovery chamber of circular profile 30mm in diameter and the other an outlet chamber with a flat wall. A magnet holder ring 12.7mm inner diameter (1/2”) was created centered on the channel-chamber junction, below where the bolus is placed, to hold a permanent magnet in place at the center of the valve. When two magnets are used, the magnet on top naturally stays in the same position due to attraction to the magnet below. On the inlet side of the channel opens into a recovery chamber shaped to allow the ferrofluid to be passively drawn back into the channel by the magnetic field after a collapse of the bolus. The model was printed on a Projet MJP 2500 (3D Systems, Rock Hill, SC), using Visijet M2G-CL and VisiJet M2 SUP as material and support respectively (3D Systems, Rock Hill, SC). Support material was removed by using an EasyClean system (3D Systems, Rock Hill, SC) and Dawn dish soap (Procter & Gamble, Cincinnati, OH) to remove residuals.

A novel passive ferrofluid check (one-way) valve | 4


Figure 2. Equipment set up

As shown in Fig. 2 and in our demonstration video[15], a basixCOMPAK 30atm pressurizing syringe (Merit Medical, South Jordan, UT) is connected to the model via a two-way stopcock (Qosina, Ronkonkoma, NY), tubing (Natvar, City of Industry, CA), and male (Injectech, Fort Collins, CO) and female luer (Qosina, Ronkonkoma, NY), allowing integration of a manometer (General Tools, Secaucus, NJ) to measure pressure. A 12.7mm x 25.4mm (1/2” x 1”) cylindrical neodymium magnet (Apex Magnets, Petersburg, WV) with a pull force of 14.6 kg (32.24 pounds) was placed inside the magnet channel by means of a tight fit and 0.2 mL of ferrofluid (Apex Magnets, Petersburg, WV) was injected into the model using a 3mL syringe (BH Supplies, Jackson, NJ).
To obtain values, pressure was applied through the pressurizing syringe, as demonstrated in a video [15]. Pressure was first applied from the outlet side of the model. The maximum pressure difference from the outlet side that the valve can withstand before collapsing, will be referred to as the sustainable pressure or collapse pressure. Pressure applied from the inlet needed to initiate flow will be referred to as the cracking pressure.
The cracking pressure was first measured by increasing the pressure difference on the inlet side until flow is initiated (at which point the valve is “open” and pushing the syringe plunger faster simply increases flow without increasing the pressure.) Then the collapse pressure was measured by increasing the pressure difference on the outlet side. At pressures below the sustainable pressure, the valve holds pressure well with no observable leaks of air in the short time (a few minutes) of our experiment. When the sustainable pressure is exceeded, the bolus explodes violently into the recovery chamber. When the pressure difference is equalized, the bolus may passively recover into the central position, or it may need to be actively “combed” with a magnet back into the central position.
The procedure was performed first with one magnet, named the “Single Magnet” configuration, placed below the channel-chamber connection. The “Dual Magnet” configuration was performed with the magnet in the same position as the Single Magnet case in the same position, but with a second magnet of the same kind placed vertically

A novel passive ferrofluid check (one-way) valve | 5

Table 1. Result pressures

| Cracking | Collapse | Pressure | Approx. Ratio:
Magnet | Pressure | Pressure | Difference | Cracking to
configuration | kPa (mmHg) | kPa (mmHg) | kPa (mmHg) | Collapse Pr.
Single | 1.1 (8) | 5.5 (41) | 4.4 (33) | 1:5
Dual | 8.5 (64) | 17.5 (131) | 8.9 (67) | 1:2

on top of the model, arranged to be strongly attracted to the lower magnet.

### 5. Results

The final pressures obtained demonstrate a clear difference between the inlet cracking pressure and outlet sustainable pressure, creating an effective passive check valve.
The ferrofluid had observable differences in behavior between the two configura-tions. After the pressure equalized following a collapse of the bolus due to exceeding the sustainable pressure, the single magnet configuration often repaired itself by drawing the fluid back into a centered bolus passively. After a collapse with two magnets, fluid further from the bolus remained stationary while the fluid closer was pulled back to the center. Following the removal of the top magnet, the stationary fluid then began to re-turn to the bolus. This is consistent with the localization of the magnetic field between two magnets, and the weakening of the magnetic field further from the channel-chamber juncture in the dual magnet configuration.
Although the dual magnet configuration demonstrated a larger absolute pressure difference due to magnetic field strength between the cracking and the collapse pressure, the single magnet configuration granted a larger ratio of collapse pressure to cracking pressure due to the much lower cracking pressure. The authors conjecture that the low cracking pressure may have been not only to the weaker magnetic field, but the weakening at the top of the 2mm high channel, which was further away from the magnet in the single magnet configuration.

### 6. Conclusions

This paper demonstrates an apparently novel passive ferrofluid one-way valve or check valve (PFCV). This valve is completely passive in that it depends entirely on the pressure at the inlet port and the outlet port. The valve has no moving parts (except for the ferrofluid, which is almost stationary), and a remarkably simple design, consisting of nothing but a channel, an inlet chamber, and outlet chamber, and a bolus of ferrofluid in a static magnetic field.
Although no effort has been made to optimize the design, the pressure difference between the cracking pressure and the sustainable back pressure appear great enough to make an effective micropump. The performance of this one-way valve may improve

A novel passive ferrofluid check (one-way) valve | 6

with additional design effort; the authors sought to publish this result as soon as it was observed. Obvious future research possibilities are:

(i) To improve the performance by varying the geometry of the passive design or shape and strength of the magnetic field.

(ii) Utilizing this design to make a micro-pump similar to earlier micro-pumps but with this simpler check valve design.
(iii) To provide an explanatory and predictive theory of operation, for example based on magnetic field strength as per [11].

(iv) Studying the ability of the valve to recover after a collapse automatically when high outlet pressure is removed, which would increase robustness in some applications.

### 7. Acknowledgements

Robert L. Read designed the PFVC. Veronica Stuckey designed, printed, and tested the model. Both authors contributed to the text of this paper.

References

[1] I Torres-D´ıaz and C Rinaldi. Recent progress in ferrofluids research: novel applications of magnetically controllable and tunable fluids. Soft matter, 10(43):8584–8602, 2014.
[2] Madhusree Kole and Sameer Khandekar. Engineering applications of ferrofluids: A review. Journal of Magnetism and Magnetic Materials, page 168222, 2021.
[3] Arzu Ozbey, Mehrdad Karimzadehkhouei, Sinan Eren Yal¸cın, Devrim Gozuacik, and Ali Ko¸sar. ¨ Modeling of ferrofluid magnetic actuation with dynamic magnetic fields in small channels. Microfluidics and Nanofluidics, 18(3):447–460, 2015.
[4] Christophe Yamahata, Mathieu Chastellain, Heinrich Hofmann, and Martin AM Gijs. A ferrofluid micropump for lab-on-a-chip applications. In Techn. Digest Eurosensors XVII, The 17th Europ. Conf. On Solid State Transducers, number CONF, 2003.
[5] Anson Hatch, Andrew Evan Kamholz, Gary Holman, Paul Yager, and Karl F Bohringer. A ferrofluidic magnetic micropump. Journal of Microelectromechanical systems, 10(2):215–221, 2001.
[6] Trevor Michelson, Joshua Rudnick, Joshua Baxter, and Reza Rashidi. A novel ferrofluid-based valve-less pump. In ASME International Mechanical Engineering Congress and Exposition, volume 59445, page V007T08A009. American Society of Mechanical Engineers, 2019.
[7] Herb Hartshorne, Christopher J Backhouse, and William E Lee. Ferrofluid-based microchip pump and valve. Sensors and Actuators B: Chemical, 99(2-3):592–600, 2004.
[8] Meng-Chun Hsu, Ahmed Alfadhel, Farzad Forouzandeh, and David A Borkholder. Biocompatible magnetic nanocomposite microcapsules as microfluidic one-way diffusion blocking valves with ultra-low opening pressure. Materials & design, 150:86–93, 2018.
[9] Christophe Yamahata, Mathieu Chastellain, Virendra K Parashar, Alke Petri, Heinrich Hofmann, and Martin AM Gijs. Plastic micropump with ferrofluidic actuation. Journal of microelectromechanical systems, 14(1):96–102, 2005.
[10] A Menz, W Benecke, R Perez-Castillejos, JA Plasza, J Esteve, N Garcia, J Higuero, and T Diez-Caballero. Fluidic components based on ferrofluids. In 1st Annual International IEEE-EMBS Special Topic Conference on Microtechnologies in Medicine and Biology. Proceedings (Cat. No. 00EX451), pages 302–306. IEEE, 2000.

A novel passive ferrofluid check (one-way) valve | 7
[11] Bruno Ando, Alberto Ascia, Salvatore Baglio, and Nicola Pitrone. | Ferrofluidic pumps: a
valuable implementation without moving parts. IEEE Transactions on Instrumentation and Measurement, 58(9):3232–3237, 2009.
[12] Eleftherios I Paschalis, James Chodosh, Ralph A Sperling, Borja Salvador-Culla, and Claes Dohlman. A novel implantable glaucoma valve using ferrofluid. PloS one, 8(6):e67404, 2013.
[13] Veronica Stuckey. | Pfcv solid model (solid works). | https://github.com/PubInv/
ferrofluidcheckvalve/blob/master/model/FerrofluidModel.SLDPRT, (https://github.com/PubInv/ferrofluidcheckvalve/blob/master/model/FerrofluidModel.SLDPRT) Nov. 2021.
[14] Veronica Stuckey. Pfcv solid model (stl). https://github.com/PubInv/ferrofluidcheckvalve/blob/master/model/FerrofluidModel.STL, (https://github.com/PubInv/ferrofluidcheckvalve/blob/master/model/FerrofluidModel.STL) Nov. 2021.
[15] Veronica Stuckey. A passive ferrofluid check valve (video). https://youtu.be/IGzz6LX1n6A, 2021.

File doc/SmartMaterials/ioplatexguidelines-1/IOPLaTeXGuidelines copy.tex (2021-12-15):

%%%%%%%%%%%%%%%%%%%%%%%%%%%%%%%%%%%%%%%%%%%%%%%%%%%%%%%%%%%%%%%%%%%%%%%%
%    INSTITUTE OF PHYSICS PUBLISHING                                   %
%                                                                      %
%   `Preparing an article for publication in an Institute of Physics   %
%    Publishing journal using LaTeX'                                   %
%                                                                      %
%    LaTeX source code `ioplau2e.tex' used to generate `author         %
%    guidelines', the documentation explaining and demonstrating use   %
%    of the Institute of Physics Publishing LaTeX preprint files       %
%    `iopart.cls, iopart12.clo and iopart10.clo'.                      %
%                                                                      %
%    `ioplau2e.tex' itself uses LaTeX with `iopart.cls'                %
%                                                                      %
%%%%%%%%%%%%%%%%%%%%%%%%%%%%%%%%%%
%
%
% First we have a character check
%
% ! exclamation mark    " double quote
% # hash                ` opening quote (grave)
% & ampersand           ' closing quote (acute)
% $ dollar              % percent
% ( open parenthesis    ) close paren.
% - hyphen              = equals sign
% | vertical bar        ~ tilde
% @ at sign             _ underscore
% { open curly brace    } close curly
% [ open square         ] close square bracket
% + plus sign           ; semi-colon
% * asterisk            : colon
% < open angle bracket  > close angle
% , comma               . full stop
% ? question mark       / forward slash
% \ backslash           ^ circumflex
%
% ABCDEFGHIJKLMNOPQRSTUVWXYZ
% abcdefghijklmnopqrstuvwxyz
% 1234567890
%
%%%%%%%%%%%%%%%%%%%%%%%%%%%%%%%%%%%%%%%%%%%%%%%%%%%%%%%%%%%%%%%%%%%
%
\documentclass[12pt]{iopart}
\newcommand{\gguide}{{\it Preparing graphics for IOP Publishing journals}}
%Uncomment next line if AMS fonts required
%\usepackage{iopams}
\begin{document}

\title[Author guidelines for IOP Publishing journals in  \LaTeXe]{How to prepare and submit an article for
publication in an IOP Publishing journal using \LaTeXe}

\author{Content \& Services Team}

\address{IOP Publishing, Temple Circus, Temple Way, Bristol BS1 6HG, UK}
\ead{submissions@iop.org}
\vspace{10pt}
\begin{indented}
\item[]August 2017
\end{indented}

\begin{abstract}
This document describes the  preparation of an article using \LaTeXe\ and
\verb"iopart.cls" (the IOP Publishing \LaTeXe\ preprint class file).
This class file is designed to help
authors produce preprints in a form suitable for submission to any of the
journals listed in table~\ref{jlab1} on the next page.  You are not obliged to use this class file---we accept
submissions using all common \LaTeX\ class and style files.  The \verb"iopart.cls"
class file is supplied merely as a convenience for those authors who find it useful.
This document gives both general advice that applies whatever class file you use, and specific advice
that applies if you choose to use \verb"iopart.cls".

We also accept submissions in Word format.  See elsewhere on this site for guidelines on Word submissions.

If you have any queries about this document or any aspect of preparing your article for submission please contact us at the e-mail address given above.
\end{abstract}

%
% Uncomment for keywords
%\vspace{2pc}
%\noindent{\it Keywords}: XXXXXX, YYYYYYYY, ZZZZZZZZZ
%
% Uncomment for Submitted to journal title message
%\submitto{\JPA}
%
% Uncomment if a separate title page is required
%\maketitle
%
% For two-column output uncomment the next line and choose [10pt] rather than [12pt] in the \documentclass declaration
%\ioptwocol
%

\section{Introduction: file preparation and submission}

The \verb"iopart" \LaTeXe\ article class file is provided to help authors prepare articles for submission to IOP Publishing journals.
  This document gives advice on preparing your submission, and specific instructions on how to use \verb"iopart.cls" to follow this advice.  You
  do not have to use \verb"iopart.cls"; articles prepared using any other common class and style files can also be submitted.
    It is not necessary to mimic the appearance of a published article.

The advice
on \LaTeX\ file preparation in this document applies to
the journals listed in table~\ref{jlab1}.  If your journal is not listed please go to the journal website via \verb"http://iopscience.iop.org/journals" for specific
submission instructions.

\begin{table}
\caption{\label{jlab1}Journals to which this document applies, and macros for the abbreviated journal names in {\tt iopart.cls}. Macros for other journal titles are listed in appendix\,A.}
\footnotesize
\begin{tabular}{@{}llll}
\br
Short form of journal title&Macro name&Short form of journal title&Macro name\\
\mr
2D Mater.&\verb"\TDM"&Mater. Res. Express&\verb"\MRE"\\
Biofabrication&\verb"\BF"&Meas. Sci. Technol.$^c$&\verb"\MST"\\
Bioinspir. Biomim.&\verb"\BB"&Methods Appl. Fluoresc.&\verb"\MAF"\\
Biomed. Mater.&\verb"\BMM"&Modelling Simul. Mater. Sci. Eng.&\verb"\MSMSE"\\
Class. Quantum Grav.&\verb"\CQG"&Nucl. Fusion&\verb"\NF"\\
Comput. Sci. Disc.&\verb"\CSD"&New J. Phys.&\verb"\NJP"\\
Environ. Res. Lett.&\verb"\ERL"&Nonlinearity$^{a,b}$&\verb"\NL"\\
Eur. J. Phys.&\verb"\EJP"&Nanotechnology&\verb"\NT"\\
Inverse Problems&\verb"\IP"&Phys. Biol.$^c$&\verb"\PB"\\
J. Breath Res.&\verb"\JBR"&Phys. Educ.$^a$&\verb"\PED"\\
J. Geophys. Eng.$^d$&\verb"\JGE"&Physiol. Meas.$^{c,d,e}$&\verb"\PM"\\
J. Micromech. Microeng.&\verb"\JMM"&Phys. Med. Biol.$^{c,d,e}$&\verb"\PMB"\\
J. Neural Eng.$^c$&\verb"\JNE"&Plasma Phys. Control. Fusion&\verb"\PPCF"\\
J. Opt.&\verb"\JOPT"&Phys. Scr.&\verb"\PS"\\
J. Phys. A: Math. Theor.&\verb"\jpa"&Plasma Sources Sci. Technol.&\verb"\PSST"\\
J. Phys. B: At. Mol. Opt. Phys.&\verb"\jpb"&Rep. Prog. Phys.$^{e}$&\verb"\RPP"\\
J. Phys: Condens. Matter&\verb"\JPCM"&Semicond. Sci. Technol.&\verb"\SST"\\
J. Phys. D: Appl. Phys.&\verb"\JPD"&Smart Mater. Struct.&\verb"\SMS"\\
J. Phys. G: Nucl. Part. Phys.&\verb"\jpg"&Supercond. Sci. Technol.&\verb"\SUST"\\
J. Radiol. Prot.$^a$&\verb"\JRP"&Surf. Topogr.: Metrol. Prop.&\verb"\STMP"\\
Metrologia&\verb"\MET"&Transl. Mater. Res.&\verb"\TMR"\\
\br
\end{tabular}\\
$^{a}$UK spelling is required; $^{b}$MSC classification numbers are required; $^{c}$titles of articles are required in journal references; $^{d}$Harvard-style references must be used (see section \ref{except}); $^{e}$final page numbers of articles are required in journal references.

\end{table}
\normalsize

Any special submission requirements for the journals are indicated with footnotes in table~\ref{jlab1}.
Journals which require references in a particular format will need special care if you are using BibTeX, and you might need to use a \verb".bst" file
that gives slightly non-standard output in order to supply any extra information required.  It is not
necessary to give references in the exact style of references used in published articles, as long as all of
the required information is present.

Also note that there is an incompatibility
between \verb"amsmath.sty" and \verb"iopart.cls" which cannot be completely worked around.  If your article relies
on commands in \verb"amsmath.sty" that are not available in \verb"iopart.cls", you may wish to consider using a different
class file.

Whatever journal you are submitting to, please look at recent published articles (preferably
articles in your subject area) to familiarize yourself with the features of the journal.  We do not demand
that your \LaTeX\ file closely resembles a published article---a generic `preprint' appearance of the sort
commonly seen on \verb"arXiv.org" is fine---but your submission should be presented
in a way that makes it easy for the referees to form an opinion of whether it is suitable for the journal.
The generic advice in this document---on what to include in an abstract, how best to present complicated
mathematical expressions, and so on---applies whatever class file you are using.

\subsection{What you will need to supply}
Submissions to our journals are handled via the ScholarOne web-based submission system.  When you submit
a new article to us you need only submit a PDF of your article.  When you submit a revised version,
we ask you to submit the source files as well.  Upon acceptance for publication we will use the source files to produce a proof of your article in the journal style.

\subsubsection{Text.}When you send us the source files for a revised version of your submission,
you should send us the \LaTeX\ source code of your paper with all figures read in by
the source code (see section \ref{figinc}).  Articles can be prepared using almost any version of \TeX\ or \LaTeX{},
not just \LaTeX\ with the class file \verb"iopart.cls".  You may split your \LaTeX\ file into several parts, but please show
which is the `master' \LaTeX\ file that reads in all of the other ones by naming it appropriately.  The `master'
\LaTeX\ file must read in all other \LaTeX\ and figure files from the current directory.  {\it Do not read in files from a different directory, e.g. \verb"" or
\verb"\include{../usr/home/smith/myfiles/macros.tex}"---we store submitted files
all together in a single directory with no subdirectories}.
\begin{itemize}
\item {\bf Using \LaTeX\ packages.} Most \LaTeXe\ packages can be used if they are
available in common distributions of \LaTeXe; however, if it is essential to use
a non-standard package then any extra files needed to process the article must
also be supplied.  Try to avoid using any packages that manipulate or change the standard
\LaTeX\ fonts: published articles use fonts in the Times family, but we prefer that you
use \LaTeX\ default Computer Modern fonts in your submission.  The use of \LaTeX\ 2.09, and of plain
\TeX\ and variants such as AMSTeX is acceptable, but a complete PDF of your submission should be supplied in these cases.
\end{itemize}
\subsubsection{Figures.} Figures should ideally be included in an article as encapsulated PostScript files
(see section \ref{figinc}) or created using standard \LaTeX\ drawing commands.
 Please name all figure files using the guidelines in section \ref{fname}.
We accept submissions that use pdf\TeX\ to include
PDF or bitmap figures, but please ensure that you send us a PDF that uses PDF version 1.4 or lower
(to avoid problems in the ScholarOne system).
You can do this by putting \verb"\pdfminorversion=4" at the very start of your TeX file.

\label{fig1}All figures should be included within the body of the text
at an appropriate point or grouped together with their captions at the end of the article. A standard graphics inclusion package such as \verb"graphicx" should be used for figure inclusion, and the package should be declared in the usual
way, for example with \verb"\usepackage{graphicx}", after the \verb"\documentclass" command.
Authors should avoid using special effects generated by including verbatim
PostScript code in the submitted \LaTeX\ file. Wherever possible, please try to use standard \LaTeX\ tools
and packages.

\subsubsection{References.\label{bibby}}
You can produce your bibliography in the standard \LaTeX\ way using the \verb"\bibitem" command. Alternatively
you can use BibTeX: our preferred  \verb".bst" styles are:

\begin{itemize}
\item For the numerical (Vancouver) reference style we recommend that authors use
 \verb"unsrt.bst"; this does not quite follow the style of published articles in our
 journals but this is not a problem.  Alternatively \verb"iopart-num.bst" created by Mark A Caprio
 produces a reference style that closely matches that in published articles.  The file is available from
\verb"http://ctan.org/tex-archive/biblio/bibtex/contrib/iopart-num/" .
\item For alphabetical (Harvard) style references we recommend that authors use the \verb"harvard.sty"
in conjunction with the \verb"jphysicsB.bst" BibTeX style file.  These, and accompanying documentation, can be downloaded
from \penalty-10000 \verb"http://www.ctan.org/tex-archive/macros/latex/contrib/harvard/".
Note that the \verb"jphysicsB.bst" bibliography style does not include article titles
in references to journal articles.
To include the titles of journal articles you can use the style \verb"dcu.bst" which is included
in the \verb"harvard.sty" package.  The output differs a little from the final journal reference
style, but all of the necessary information is present and the reference list will be formatted
into journal house style as part of the production process if your article is accepted for publication.
\end{itemize}

\noindent Please make sure that you include your \verb".bib" bibliographic database file(s) and any
\verb".bst" style file(s) you have used.

\subsection{\label{copyright}Copyrighted material and ethical policy} If you wish to make use of previously published material for which you do not own the copyright then you must seek permission from the copyright holder, usually both the author and the publisher.  It is your responsibility to obtain copyright permissions and this should be done prior to submitting your article. If you have obtained permission, please provide full details of the permission granted---for example, copies of the text of any e-mails or a copy of any letters you may have received. Figure captions must include an acknowledgment of the original source of the material even when permission to reuse has been obtained.  Please read our ethical policy before writing your article.

\subsection{Naming your files}
\subsubsection{General.}
Please name all your files, both figures and text, as follows:
\begin{itemize}
\item Use only characters from the set a to z, A to Z, 0 to 9 and underscore (\_).
\item Do not use spaces or punctuation characters in file names.
\item Do not use any accented characters such as
\'a, \^e, \~n, \"o.
\item Include an extension to indicate the file type (e.g., \verb".tex", \verb".eps", \verb".txt", etc).
\item Use consistent upper and lower case in filenames and in your \LaTeX\ file.
If your \LaTeX\ file contains the line \verb"" the figure file must be called
\verb"fig1.eps" and not \verb"Fig1.eps" or \verb"fig1.EPS".  If you are on a Unix system, please ensure that
there are no pairs of figures whose names differ only in capitalization, such as \verb"fig_2a.eps" and \verb"fig_2A.eps",
as Windows systems will be unable to keep the two files in the same directory.
\end{itemize}
When you submit your article files, they are manipulated
and copied many times across multiple databases and file systems. Including non-standard
characters in your filenames will cause problems when processing your article.
\subsubsection{\label{fname}Naming your figure files.} In addition to the above points, please give each figure file a name which indicates the number of the figure it contains; for example, \verb"figure1.eps", \verb"figure2a.eps", etc. If the figure file contains a figure with multiple parts, for example figure 2(a) to 2(e), give it a name such as \verb"figure2a_2e.eps", and so forth.
\subsection{How to send your files}
Please send your submission via the ScholarOne submission system.  Go to the journal home
page, and use the `Submit an article' link on the right-hand side.

\section{Preparing your article}

\subsection{Sample coding for the start of an article}
\label{startsample}
The code for the start of a title page of a typical paper in the \verb"iopart.cls" style might read:
\small\begin{verbatim}
\documentclass[12pt]{iopart}
\begin{document}
\title[The anomalous magnetic moment of the
neutrino]{The anomalous magnetic moment of the
neutrino and its relation to the solar neutrino problem}

\author{P J Smith$^1$, T M Collins$^2$,
R J Jones$^3$\footnote{Present address:
Department of Physics, University of Bristol, Tyndalls Park Road,
Bristol BS8 1TS, UK.} and Janet Williams$^3$}

\address{$^1$ Mathematics Faculty, Open University,
Milton Keynes MK7~6AA, UK}
\address{$^2$ Department of Mathematics,
Imperial College, Prince Consort Road, London SW7~2BZ, UK}
\address{$^3$ Department of Computer Science,
University College London, Gower Street, London WC1E~6BT, UK}
\ead{williams@ucl.ac.uk}

\begin{abstract}
...
\end{abstract}
\keywords{magnetic moment, solar neutrinos, astrophysics}
\submitto{\jpg}
\maketitle
\end{verbatim}
\normalsize

At the start of the \LaTeX\ source code please include
commented material to identify the journal, author, and (if you are sending a revised
version or a resubmission) the reference number that the journal
has given to the submission. The first non-commented line should be
\verb"\documentclass[12pt]{iopart}"  to load the preprint class
file.  The normal text will be in the Computer Modern 12pt font.
It is possible to specify 10pt font size by passing the option \verb"[10pt]" to the class file.
Although it is possible to choose a font other than Computer Modern by loading external packages, this is not recommended.

The article text begins after \verb"\begin{document}".
Authors of very long articles may find it convenient to separate
their article into a series of \LaTeX\ files each containing one section, and each of which is called
in turn by the primary file.  The files for each section should be read in from the current directory;
please name the primary file clearly so that we know to run \LaTeX\ on this file.

Authors may use any common \LaTeX\ \verb".sty" files.
Authors may also define their own macros and definitions either in the main article \LaTeX\ file
or in a separate \verb".tex" or \verb".sty" file that is read in by the
main file, provided they do not overwrite existing definitions.
It is helpful to the production staff if complicated author-defined macros are explained in a \LaTeX\ comment.
The article class \verb"iopart.cls" can be used with other package files such
as those loading the AMS extension fonts
\verb"msam" and \verb"msbm", which provide the
blackboard bold alphabet and various extra maths symbols as well as symbols useful in figure
captions.  An extra style file \verb"iopams.sty" is provided to load these
packages and provide extra definitions for bold Greek letters.

\subsection{\label{dblcol}Double-column layout}
The \verb"iopart.cls" class file produces single-column output by default, but a two-column layout can be obtained by
using \verb"\documentclass[10pt]" at the start of the file and \verb"\ioptwocol" after the \verb"\maketitle" command.  Two-column output will begin
on a new page (unlike in published double-column articles, where the two-column material
starts on the same page as the abstract).

In general we prefer to receive submissions in single-column format even for journals
published in double-column style; however, the \verb"\ioptwocol" option may be useful to test figure sizes
and equation breaks for these journals.  When setting material
in two columns you can use the asterisked versions of \LaTeX\ commands such as \verb"\begin{figure*} ... \end{figure*}"
to set figures and tables across two columns.  If you have any problems or any queries about producing two-column output, please contact us at \verb"submissions@iop.org".

\section{The title and abstract page}
If you use \verb"iopart.cls", the code for setting the title page information is slightly different from
the normal default in \LaTeX.  If you are using a different class file, you do not need to mimic the appearance of
an \verb"iopart.cls" title page, but please ensure that all of the necessary information is present.

\subsection{Titles and article types}
The title is set using the command
\verb"\title{#1}", where \verb"#1" is the title of the article. The
first letter
of the title should be capitalized with the rest in lower case.
The title appears in bold case, but mathematical expressions within the title may be left in light-face type.

If the title is too long to use as a running head at the top of each page (apart from the
first) a short
form can be provided as an optional argument (in square brackets)
before the full title, i.e.\ \verb"\title[Short title]{Full title}".

For article types other than papers, \verb"iopart.cls"
has a generic heading \verb"\article[Short title]{TYPE}{Full title}"
and some specific definitions given in table~\ref{arttype}. In each case (apart from Letters
to the Editor and Fast Track Communications) an
optional argument can be used immediately after the control sequence name
to specify the short title; where no short title is given, the full title
will be used as the running head.  Not every article type has its own macro---use \verb"\article" for
any not listed.  A full list of the types of articles published by a journal is given
in the submission information available via the journal home page.
%For Letters use \verb"\letter{Full title}"; no short title is required as
%the running head is automatically defined to be {\it Letter to the Editor}.
The generic heading could be used for
articles such as those presented at a conference or workshop, e.g.
\small\begin{verbatim}
\article[Short title]{Workshop on High-Energy Physics}{Title}
\end{verbatim}\normalsize
Footnotes to titles may be given by using \verb"\footnote{Text of footnote.}" immediately after the title.
Acknowledgment of funding should be included in the acknowledgments section rather than in a footnote.

\begin{table}
\caption{\label{arttype}Types of article defined in the {\tt iopart.cls}
class file.}
\footnotesize\rm
\begin{tabular*}{\textwidth}{@{}l*{15}{@{\extracolsep{0pt plus12pt}}l}}
\br
Command& Article type\\
\mr
\verb"\title{#1}"&Paper (no surtitle on first page)\\
\verb"\ftc{#1}"&Fast Track Communication\\
\verb"\review{#1}"&Review\\
\verb"\topical{#1}"&Topical Review\\
\verb"\comment{#1}"&Comment\\
\verb"\note{#1}"&Note\\
\verb"\paper{#1}"&Paper (no surtitle on first page)\\
\verb"\prelim{#1}"&Preliminary Communication\\
\verb"\rapid{#1}"&Rapid Communication\\
\verb"\letter{#1}"&Letter to the Editor\\
\verb"\article{#1}{#2}"&Other articles\\\ & (use this for any other type of article; surtitle is whatever is entered as {\tt
\#1})\\
\br
\end{tabular*}
\end{table}

\subsection{Authors' names and addresses}
For the authors' names type \verb"\author{#1}",
where \verb"#1" is the
list of all authors' names. Western-style names should be written as initials then
family name, with a comma after all but the last
two names, which are separated by `and'. Initials should {\it not} be followed by full stops. First (given) names may be used if
desired.  Names in Chinese, Japanese and Korean styles should be written as you want them to appear in the published article. Authors in all IOP Publishing journals have the option to include their names in Chinese, Japanese or Korean characters in addition to the English name: see appendix B for details.

If the authors are at different addresses a superscripted number, e.g. $^1$, \verb"$^1$", should be used after each
name to reference the author to his/her address.
If an author has additional information to appear as a footnote, such as
a permanent address, a normal \LaTeX\ footnote command
should be given after the family name and address marker
with this extra information.

The authors' affiliations follow the list of authors.
Each address is set by using
\verb"\address{#1}" with the address as the single parameter in braces.
If there is more
than one address then the appropriate superscripted number, followed by a space, should come at the start of
the address.

E-mail addresses are added by inserting the
command \verb"\ead{#1}" after the postal address(es) where \verb"#1" is the e-mail address.
See section~\ref{startsample} for sample coding. For more than one e-mail address, please use the command
\verb"\eads{\mailto{#1}, \mailto{#2}}" with \verb"\mailto" surrounding each e-mail address.  Please ensure
that, at the very least, you state the e-mail address of the corresponding author.

\subsection{The abstract}
The abstract follows the addresses and
should give readers concise information about the content
of the article and indicate the main results obtained and conclusions
drawn. It should be self-contained---there should be no references to
figures, tables, equations, bibliographic references etc.  It should be enclosed between \verb"\begin{abstract}"
and \verb"\end{abstract}" commands.  The abstract should normally be restricted
to a single paragraph of around 200 words.

\subsection{Subject classification numbers}
We no longer ask authors to supply Physics and Astronomy Classification System (PACS)
classification numbers.  For submissions to {\it Nonlinearity}\/ we ask that you should
supply Mathematics Subject Classification (MSC) codes.  MSC numbers are included after the abstract
using \verb"\ams{#1}".

The command
\verb"\submitto{#1}" can be inserted, where \verb"#1" is the journal name written in full or the appropriate control sequence as
given in table~\ref{jlab1}. This command is not essential to the running of the file and can be omitted.

\subsection{Keywords}
Keywords are required for all submissions. Authors should supply a minimum of three (maximum seven) keywords appropriate to their article as a new paragraph starting \verb"\noindent{\it Keywords\/}:" after the end of the abstract.

\subsection{Making a separate title page}
To keep the header material on a separate page from the
body of the text insert \verb"\maketitle" (or \verb"\newpage") before the start of the text.
If \verb"\maketitle" is not included the text of the
article will start immediately after the abstract.

\section{The text}
\subsection{Sections, subsections and subsubsections}
The text of articles may be divided into sections, subsections and, where necessary,
subsubsections. To start a new section, end the previous paragraph and
then include \verb"\section" followed by the section heading within braces.
Numbering of sections is done {\it automatically} in the headings:
sections will be numbered 1, 2, 3, etc, subsections will be numbered
2.1, 2.2,  3.1, etc, and subsubsections will be numbered 2.3.1, 2.3.2,
etc.  Cross references to other sections in the text should, where
possible, be made using
labels (see section~\ref{xrefs}) but can also
be made manually. See section~\ref{eqnum} for information on the numbering of displayed equations. Subsections and subsubsections are
similar to sections but
the commands are \verb"\subsection" and \verb"\subsubsection" respectively.
Sections have a bold heading, subsections an italic heading and
subsubsections an italic heading with the text following on directly.
\small\begin{verbatim}
\section{This is the section title}
\subsection{This is the subsection title}
\end{verbatim}\normalsize

The first section is normally an introduction,  which should state clearly
the object of the work, its scope and the main advances reported, with
brief references to relevant results by other workers. In long papers it is
helpful to indicate the way in which the paper is arranged and the results
presented.

Footnotes should be avoided whenever possible and can often be included in the text as phrases or sentences in parentheses. If required, they should be used only for brief notes that do not fit conveniently into the text. The use of
displayed mathematics in footnotes should be avoided wherever possible and no equations within a footnote should be numbered.
The standard \LaTeX\ macro \verb"\footnote" should be used.  Note that in \verb"iopart.cls" the \verb"\footnote" command
produces footnotes indexed by a variety of different symbols,
whereas in published articles we use numbered footnotes.  This
is not a problem: we will convert symbol-indexed footnotes to numbered ones during the production process.

\subsection{Acknowledgments}
Authors wishing to acknowledge assistance or encouragement from
colleagues, special work by technical staff or financial support from
organizations should do so in an unnumbered `Acknowledgments' section
immediately following the last numbered section of the paper. In \verb"iopart.cls" the
command \verb"\ack" sets the acknowledgments heading as an unnumbered
section.

Please ensure that you include all of the sources of funding and the funding contract reference numbers that you are contractually obliged to acknowledge. We often receive requests to add such information very late in the production process, or even after the article is published, and we cannot always do this. Please collect all of the necessary information from your co-authors and sponsors as early as possible.

\subsection{Appendices}
Technical detail that it is necessary to include, but that interrupts
the flow of the article, may be consigned to an appendix.
Any appendices should be included at the end of the main text of the paper, after the acknowledgments section (if any) but before the reference list.
If there are
two or more appendices they should be called Appendix A, Appendix B, etc.
Numbered equations will be in the form (A.1), (A.2), etc,
figures will appear as figure A1, figure B1, etc and tables as table A1,
table B1, etc.

The command \verb"\appendix" is used to signify the start of the
appendices. Thereafter \verb"\section", \verb"\subsection", etc, will
give headings appropriate for an appendix. To obtain a simple heading of
`Appendix' use the code \verb"\section*{Appendix}". If it contains
numbered equations, figures or tables the command \verb"\appendix" should
precede it and \verb"\setcounter{section}{1}" must follow it.

\subsection{Some matters of style}
It will help the readers if your article is written in a clear,
consistent and concise manner. During the production process
we will try to make sure that your work is presented to its
readers in the best possible way without sacrificing the individuality of
your writing. Some recommended
points to note, however, are the following.  These apply to all of the journals listed
in table~\ref{jlab1}.
\begin{enumerate}
\item Authors are often inconsistent in the use of `ize' and `ise' endings.
We recommend using `-ize' spellings (diagonalize,
renormalization, minimization, etc) but there are some common
exceptions to this, for example: devise,
promise and advise.

\item The words table and figure should be written
in full and {\bf not} abbreviaged to tab. and fig. Do not include `eq.', `equation' etc before an equation number or `ref.'\, `reference' etc before a reference number.
\end{enumerate}

Please check your article carefully for accuracy, consistency and clarity before
submission. Remember that your article will probably be read by many
people whose native language is not English and who may not
be aware of many of the subtle meanings of words or idiomatic phases
present in the English language. It therefore helps if you try to keep
sentences as short and simple as possible.  If you are not a native English speaker,
please ask a native English speaker to read your paper and check its grammar.

\section{Mathematics}
\subsection{Two-line constructions}
The great advantage of \LaTeX\
over other text processing systems is its
ability to handle mathematics of almost any degree of complexity. However,
in order to produce an article suitable for publication both within a print journal and online,
authors should exercise some restraint on the constructions used. Some equations using very small characters which are clear in a preprint style article may be difficult read in a smaller format.

For simple fractions in the text the solidus \verb"/", as in
$\lambda/2\pi$, should be used instead of \verb"\frac" or \verb"\over",
using parentheses where necessary to avoid ambiguity,
for example to distinguish between $1/(n-1)$ and $1/n-1$. Exceptions to
this are the proper fractions $\frac12$, $\frac13$, $\frac34$,
etc, which are better left in this form. In displayed equations
horizontal lines are preferable to solidi provided the equation is
kept within a height of two lines. A two-line solidus should be
avoided where possible; the construction $(\ldots)^{-1}$ should be
used instead. For example use:
\begin{equation*}
\frac{1}{M_{\rm a}}\left(\int^\infty_0{\rm d}
\omega\;\frac{|S_o|^2}{N}\right)^{-1}\qquad\mbox{instead of}\qquad
\frac{1}{M_{\rm a}}\biggl/\int^\infty_0{\rm d}
\omega\;\frac{|S_o|^2}{N}.
\end{equation*}

\subsection{Roman and italic in mathematics}
In mathematics mode \LaTeX\ automatically sets variables in an italic
font. In most cases authors should accept this italicization. However,
there are some cases where it is preferable to use a Roman font; for
instance, a Roman d for a differential d, a Roman e
for an exponential e and a Roman i for the square root of $-1$. To
accommodate this and to simplify the  typing of equations, \verb"iopart.cls" provides
some extra definitions. \verb"\rmd", \verb"\rme" and \verb"\rmi"
now give Roman d, e and i respectively for use in equations,
e.g.\ $\rmi x\rme^{2x}\rmd x/\rmd y$
is obtained by typing \verb"$\rmi x\rme^{2x}\rmd x/\rmd y$".

Certain other common mathematical functions, such as cos, sin, det and
ker, should appear in Roman type. Standard \LaTeX\ provides macros for
most of these functions
(in the cases above, \verb"\cos", \verb"\sin", \verb"\det" and \verb"\ker"
respectively); \verb"iopart.cls" also provides
additional definitions for $\Tr$, $\tr$ and
$\Or$ (\verb"\Tr", \verb"\tr" and \verb"\Or", respectively).

Subscripts and superscripts should be in Roman type if they are labels
rather than variables or characters that take values. For example in the
equation
\[
\epsilon_m=-g\mu_{\rm n}Bm
\]
$m$, the $z$ component of the nuclear spin, is italic because it can have
different values whereas n is Roman because it
is a label meaning nuclear ($\mu_{\rm n}$
is the nuclear magneton).

\subsection{Displayed equations in double-column journals}
Authors should bear in mind that all mathematical formulae in double-column journals will need to fit
into the width of a single column.  You may find it helpful to use a two-column layout (such as the two-column
option in \verb"iopart.cls") in your submission so that you can check the width of equations.

\subsection{Special characters for mathematics}
Bold italic characters can be used in our journals to signify vectors (rather
than using an upright bold or an over arrow). To obtain this effect when using \verb"iopart.cls",
use \verb"\bi{#1}" within maths mode, e.g. $\bi{ABCdef}$. Similarly, in \verb"iopart.cls", if upright
bold characters are required in maths, use \verb"\mathbf{#1}" within maths
mode, e.g. $\mathbf{XYZabc}$. The calligraphic (script) uppercase alphabet
is obtained with \verb"\mathcal{AB}" or \verb"\cal{CD}"
($\mathcal{AB}\cal{CD}$).

The American Mathematical Society provides a series of extra symbol fonts
to use with \LaTeX\ and packages containing the character definitions to
use these fonts. Authors wishing to use Fraktur
\ifiopams$\mathfrak{ABC}$ \fi
or Blackboard Bold \ifiopams$\mathbb{XYZ}$ \fi can include the appropriate
AMS package (e.g. \verb"amsgen.sty", \verb"amsfonts.sty", \verb"amsbsy.sty", \verb"amssymb.sty") with a
\verb"\usepackage" command or add the command \verb"\usepackage{iopams}"
which loads the four AMS packages mentioned above and also provides
definitions for extra bold characters (all Greek letters and some other
additional symbols).

The package \verb"iopams.sty" uses the definition \verb"\boldsymbol" in \verb"amsbsy.sty"
which allows individual non-alphabetical symbols and Greek letters to be
made bold within equations.
The bold Greek lowercase letters \ifiopams$\balpha \ldots\bomega$,\fi
are obtained with the commands
\verb"\balpha" \dots\ \verb"\bomega" (but note that
bold eta\ifiopams, $\bfeta$,\fi\ is \verb"\bfeta" rather than \verb"\beta")
and the capitals\ifiopams, $\bGamma\ldots\bOmega$,\fi\ with commands
\verb"\bGamma" \dots\
\verb"\bOmega". Bold versions of the following symbols are
predefined in \verb"iopams.sty":
bold partial\ifiopams, $\bpartial$,\fi\ \verb"\bpartial",
bold `ell'\ifiopams, $\bell$,\fi\  \verb"\bell",
bold imath\ifiopams, $\bimath$,\fi\  \verb"\bimath",
bold jmath\ifiopams, $\bjmath$,\fi\  \verb"\bjmath",
bold infinity\ifiopams, $\binfty$,\fi\ \verb"\binfty",
bold nabla\ifiopams, $\bnabla$,\fi\ \verb"\bnabla",
bold centred dot\ifiopams, $\bdot$,\fi\  \verb"\bdot". Other
characters are made bold using
\verb"\boldsymbol{\symbolname}".

Please do not use the style file \verb"amsmath.sty" (part of the AMSTeX package) in conjunction with \verb"iopart.cls". This will result in several errors. To make use of the macros defined in \verb"amsmath.sty", \verb"iopart.cls" provides the file \verb"setstack.sty" which reproduces the following useful macros from \verb"amsmath.sty":
\small\begin{verbatim}
\overset \underset \sideset \substack \boxed   \leftroot
\uproot  \dddot    \ddddot  \varrow   \harrow
\end{verbatim}\normalsize

If the mathematical notation
that you need is best handled in \verb"amsmath.sty" you might want to consider using an article class
other than \verb"iopart.cls". We accept submissions using any class or style files.

Table~\ref{math-tab2} lists some other macros for use in
mathematics with a brief description of their purpose.

\begin{table}
\caption{\label{math-tab2}Other macros defined in {\tt iopart.cls} for use in maths.}
\begin{tabular*}{\textwidth}{@{}l*{15}{@{\extracolsep{0pt plus
12pt}}l}}
\br
Macro&Result&Description\\
\mr
\verb"\fl"&&Start line of equation full left\\
\verb"\case{#1}{#2}"&$\case{\#1}{\#2}$&Text style fraction in display\\
\verb"\Tr"&$\Tr$&Roman Tr (Trace)\\
\verb"\tr"&$\tr$&Roman tr (trace)\\
\verb"\Or"&$\Or$&Roman O (of order of)\\
\verb"\tdot{#1}"&$\tdot{x}$&Triple dot over character\\
\verb"\lshad"&$\lshad$&Text size left shadow bracket\\
\verb"\rshad"&$\rshad$&Text size right shadow bracket\\
\br
\end{tabular*}
\end{table}

\subsection{Alignment of displayed equations}

The normal style for aligning displayed equations in our published journal articles is to align them left rather than centre. The \verb"iopart.cls" class file automatically does this and indents each line of a display.  In \verb"iopart.cls", to make any line start at the left margin of the page, add \verb"\fl" at start of the line (to indicate full left).

Using the \verb"eqnarray" environment equations will naturally be aligned left and indented without the use of any ampersands for alignment, see equations (\ref{eq1}) and (\ref{eq2})
\begin{eqnarray}
\alpha + \beta =\gamma^2, \label{eq1}\\
\alpha^2 + 2\gamma + \cos\theta = \delta. \label{eq2}
\end{eqnarray}
This is the normal equation style for our journals.

Where some secondary alignment is needed, for instance a second part of an equation on a second line, a single ampersand is added at the point of alignment in each line  (see  (\ref{eq3}) and (\ref{eq4})).
\begin{eqnarray}
\alpha &=2\gamma^2 + \cos\theta + \frac{XY \sin\theta}{X+ Y\cos\theta} \label{eq3}\\
 & = \delta\theta PQ \cos\gamma. \label{eq4}
\end{eqnarray}

Two points of alignment are possible using two ampersands for alignment (see  (\ref{eq5}) and (\ref{eq6})).  Note in this case extra space \verb"\qquad" is added before the second ampersand in the longest line (the top one) to separate the condition from the equation.
\begin{eqnarray}
\alpha &=2\gamma^2 + \cos\theta + \frac{XY \sin\theta}{X+ Y\cos\theta}\qquad& \theta > 1 \label{eq5}\\
 & = \delta\theta PQ \cos\gamma &\theta \leq 1.\label{eq6}
\end{eqnarray}

For a long equation which has to be split over more than one line the first line should start at the left margin, this is achieved by inserting \verb"\fl" (full left) at the start of the line. The use of the alignment parameter \verb"&" is not necessary unless some secondary alignment is needed.
\begin{eqnarray}
\fl \alpha + 2\gamma^2 = \cos\theta + \frac{XY \sin\theta}{X+ Y\cos\theta} +  \frac{XY \sin\theta}{X- Y\cos\theta} +
+ \left(\frac{XY \sin\theta}{X+ Y\cos\theta}\right)^2 \nonumber\\
+  \left(\frac{XY \sin\theta}{X- Y\cos\theta}\right)^2.\label{eq7}
\end{eqnarray}

The plain \TeX\ command \verb"\eqalign" can be used within an \verb"equation" environment to obtain a multiline equation with a single centred number, for example
\begin{equation}
\eqalign{\alpha + \beta =\gamma^2 \cr
\alpha^2 + 2\gamma + \cos\theta = \delta.}
\end{equation}

During the production process we will break equations as appropriate for the page layout of the journal. If you are submitting to a double-column journal and wish to review how your equations will break, you may find the double-column layout described in section \ref{dblcol} useful.

\subsection{Miscellaneous points}
The following points on the layout of mathematics apply whichever class file you use.

Exponential expressions, especially those containing subscripts or
superscripts, are clearer if the notation $\exp(\ldots)$ is used, except for
simple examples. For instance $\exp[\rmi(kx-\omega t)]$ and $\exp(z^2)$ are
preferred to $\e^{\rmi(kx-\omega t)}$ and $\e^{z^2}$, but
$\e^x$
is acceptable.

Similarly the square root sign $\sqrt{\phantom{b}}$ should
only be used with relatively
simple expressions, e.g.\ $\sqrt2$ and $\sqrt{a^2+b^2}$;
in other cases the
power $1/2$ should be used; for example, $[(x^2+y^2)/xy(x-y)]^{1/2}$.

It is important to distinguish between $\ln = \log_\e$ and $\lg
=\log_{10}$. Braces, brackets and parentheses should be used in the
following order: $\{[(\;)]\}$. The same ordering of brackets should be
used within each size. However, this ordering can be ignored if the
brackets have a
special meaning (e.g.\ if they denote an average or a function).

Decimal fractions should always be preceded by a zero: for example 0.123 {\bf not} .123.
For long numbers use thin spaces after every third character away from the position of the decimal point, unless
this leaves a single separated character: e.g.\ $60\,000$, $0.123\,456\,78$
but 4321 and 0.7325.

Equations should be followed by a full stop (periods) when at the end
of a sentence.

\subsection{Equation numbering and layout in {\tt iopart.cls}}
\label{eqnum}
\LaTeX\ provides facilities for automatically numbering equations
and these should be used where possible. Sequential numbering (1), (2),
etc, is the default numbering system although in \verb"iopart.cls", if the command
\verb"\eqnobysec" is included in the preamble, equation numbering
by section is obtained, e.g.\
(2.1), (2.2), etc. Equation numbering by section is used in appendices automatically when the \verb"\appendix" command is used, even if sequential numbering has been used in the rest of the article.
Refer to equations in the text using the equation number in parentheses. It is not normally necessary to include the word equation before the number; and abbreviations such as eqn or eq should not be used.
In \verb"iopart.cls", there are alternatives to the standard \verb"\ref" command that you might
find useful---see \tref{abrefs}.

Sometimes it is useful to number equations as parts of the same
basic equation. This can be accomplished in \verb"iopart.cls" by inserting the
commands \verb"\numparts" before the equations concerned and
\verb"\endnumparts" when reverting to the normal sequential numbering.
For example using \verb"\numparts \begin{eqnarray}" ... \verb"\end{eqnarray} \endnumparts":

\numparts
\begin{eqnarray}
T_{11}&=(1+P_\e)I_{\uparrow\uparrow}-(1-P_\e)
I_{\uparrow\downarrow},\label{second}\\
T_{-1-1}&=(1+P_\e)I_{\downarrow\downarrow}-(1-P_\e)I_{\uparrow\downarrow},\\
S_{11}&=(3+P_\e)I_{\downarrow\uparrow}-(3-P_e)I_{\uparrow\uparrow},\\
S_{-1-1}&=(3+P_\e)I_{\uparrow\downarrow}-(3-P_\e)
I_{\downarrow\downarrow}.
\end{eqnarray}
\endnumparts

Equation labels within the \verb"\eqnarray" environment will be referenced
as subequations, e.g. (\ref{second}).

\subsection{Miscellaneous extra commands for displayed equations}
The \verb"\cases" command has been amended slightly in \verb"iopart.cls" to
increase the space between the equation and the condition.
\Eref{cases}
demonstrates simply the output from the \verb"\cases" command
\begin{equation}
\label{cases}
X=\cases{1&for $x \ge 0$\\
-1&for $x<0$\\}
\end{equation}
%The code used was:
%\small\begin{verbatim}
%\begin{equation}
%\label{cases}
%X=\cases{1&for $x \ge 0$\\
%-1&for $x<0$\\}
%\end{equation}
%\end{verbatim}
%\normalsize

To obtain text style fractions within displayed maths the command
\verb"\case{#1}{#2}" can be used instead
of the usual \verb"\frac{#1}{#2}" command or \verb"{#1 \over #2}".

When two or more short equations are on the same line they should be
separated by a `qquad space' (\verb"\qquad"), rather than
\verb"\quad" or any combination of \verb"\,", \verb"\>", \verb"\;"
and \verb"\ ".

\section{Referencing\label{except}}
Two different styles of referencing are in common use:
the Harvard alphabetical system and the Vancouver numerical system.
All journals to which this document applies allow the use of either the Harvard or Vancouver system,
except for {\it Physics in Medicine and Biology} and {\it Physiological Measurement}
for which authors {\it must\/} use the Harvard referencing style (with the titles of journal
articles given, and final page numbers given).

\subsection{Harvard (alphabetical) system}
In the Harvard system the name of the author appears in the text together
with the year of publication. As appropriate, either the date or the name
and date are included within parentheses. Where there are only two authors
both names should be given in the text; if there are more than two
authors only the first name should appear followed by `{\it et al}'
(which can be obtained in \verb"iopart.cls" by typing \verb"\etal"). When two or
more references to work by one author or group of authors occur for the
same year they should be identified by including a, b, etc after the date
(e.g.\ 2012a). If several references to different pages of the same article
occur the appropriate page number may be given in the text, e.g.\ Kitchen
(2011, p 39).

The reference list at the end of an article consists of an
unnumbered `References' section containing an
alphabetical listing by authors' names. References with the same author list are ordered by date, oldest first.
The reference list in the
preprint style is started in \verb"iopart.cls" by including the command \verb"\section*{References}" and then
\verb"\begin{harvard}".
Individual references start with \verb"\item[]" and the reference list is completed with \verb"\end{harvard}".
There is also a shortened form of the coding: \verb"\section*{References}"
and \verb"\begin{harvard}" can be replaced by the single command
\verb"\References", and \verb"\end{harvard}" can be shortened to
\verb"\endrefs".

\subsection{Vancouver (numerical) system}
In the Vancouver system references are numbered sequentially
throughout the text. The numbers occur within square brackets and one
number can be used to designate several references. A numerical
reference list in the \verb"iopart" style is started by including the
command \verb"\section*{References}" and then
\verb"\begin{thebibliography}{<num>}", where \verb"<num>" is the largest
number in the reference list (or any other number with the same number
of digits).  The
reference list gives the references in
numerical order, individual references start with \verb"\bibitem{label}". The list is completed by
\verb"\end{thebibliography}". Short forms of the commands are again
available: \verb"\Bibliography{<num>}" can be used at the start of the
references section and \verb"\endbib" at the end.

A variant of this system is to use labels instead of numbers within
square brackets, in this case references in the list should start with \verb"\bibitem[label-text]". This method is allowed for all journals that accept numerical references.

\subsection{BibTeX\label{bibtex}}
If you are using BibTeX, see the earlier section \ref{bibby} for information on what \verb".bst" file to use.
The output that you get will differ slightly from that specified in the rest of this section,
but this is not a problem as long as all the relevant information is present.

\subsection{References, general}
A complete reference should provide the reader with enough information to
locate the item concerned. Up to ten authors may be given in a particular reference; where
there are more than ten only the first should be given followed by
`{\it et al}'.  If you are using BibTeX
and the \verb".bst" file that you are using includes more than 10 authors, do not worry about this:
we can correct this during the production process.  Abbreviate a journal name only in accordance with the journal's
own recommendations for abbreviation---if in doubt, leave it unabbreviated.

The terms {\it loc.\ cit.}\ and {\it ibid}.\ should not be used.
Unpublished conferences and reports should generally not be included
in the reference list if a published version of the work exists. Articles in the course of publication should
include the article title and the journal of publication, if known.
A reference to a thesis submitted for a higher degree may be included
if it has not been superseded by a published
paper---please state the institution where the work was submitted.

The basic structure of a reference in the reference list is the same in both the alphabetical and numerical systems, the only difference being the code at the start of the reference. Alphabetical references are preceded by \verb"\item[]", numerical by \verb"\bibitem{label}" or just \verb"\item" to generate a number or \verb"\nonum" where a reference is not the first in a group of references under the same number.

Note that footnotes to the text should not be
included in the reference list, but should appear at the bottom of the relevant page by using the \verb"\footnote" command.

\subsection{References to journal articles}
The following guidance applies if you are producing your reference list `by hand'; that is,
without the help of BibTeX.  See section~\ref{bibby} for BibTeX help.

Article references in published articles in our journals contain three changes of
font:
the authors and date appear in Roman type, the journal title in
italic, the volume number in bold and the page numbers in Roman again.
A typical journal entry would be:

\smallskip
\begin{harvard}
\item[] Spicer P E, Nijhoff F W and van der Kamp P H 2011 {\it Nonlinearity} {\bf 24} 2229
\end{harvard}
\smallskip

\noindent which would be obtained by typing, within the references
environment
\small\begin{verbatim}
\item[] Spicer P E, Nijhoff F W and van der Kamp P H 2011 {\it Nonlinearity}
{\bf 24} 2229
\end{verbatim}\normalsize

\noindent Features to note are the following.

\begin{enumerate}
\item The authors should be in the form of surname (with only the first
letter capitalized) followed by the initials with no
periods after the initials. Authors should be separated by a comma
except for the last two which should be separated by `and' with no
comma preceding it.

\item The year of publication follows the authors and is not in parentheses.

\item Titles of journal articles can also be included (in Roman (upright) text after the year). Article titles are required in reference lists for {\it Inverse Problems, Journal of Neural Engineering, Measurement Science and Technology, Physical Biology, Physics in Medicine and Biology\/} and {\it Physiological Measurement}.

\item The journal is in italic and is abbreviated. If a journal has several parts denoted by
different letters the part letter should be inserted after the journal in Roman type (e.g.\
{\it Phys.\ Rev.\ \rm A}). \verb"iopart.cls" includes macros for abbreviated titles of all journals handled by IOP Publishing (see table~\ref{jlab2}) and some other common titles (table \ref{jlab3}).

\item The volume number is bold; the page number is Roman.
 Both the initial and final page numbers should be given where possible---note that for {\it Reports on Progress in Physics\/}, {\it Physiological Measurement} and {\it Physics in Medicine and Biology}
 the final page number is {\it required}. The final page number should be in
the shortest possible form and separated from the initial page number by an en rule (\verb"--"), e.g.\ 1203--14.

\item Where there are two or more references with identical authors,
the authors' names should be repeated for the second and subsequent references. Each individual publication should be presented as a separate reference, although in the numerical system one number can be used for several references. This facilitates linking in the online journal.
\end{enumerate}

\subsubsection{Article numbering.}
Many journals now use article-numbering systems that do not fit the conventional {\it year-journal-volume-page numbers} pattern. Some examples are:

\numrefs{1}
\item Carlip S and Vera R 1998 {\it Phys. Rev.} D {\bf 58} 011345
\item Davies K and Brown G 1997 {\it J. High Energy Phys.} JHEP12(1997)002
\item Hannestad S 2005 {\it J. Cosmol. Astropart. Phys.} JCAP02(2005)011
\item Hilhorst H J 2005 {\it J. Stat. Mech.} L02003
\item Gundlach C 1999 {\it Liv. Rev. Rel.} 1994-4
\endnumrefs

\noindent The website of the journal you are citing should state the correct format for citations.

\subsection{Preprint references}
Preprints may be referenced but if the article concerned has been published in a peer-reviewed journal, that reference should take precedence. If only a preprint reference can be given, it is helpful to include the article title. Examples are:
\vskip6pt
\numrefs{1}
\item Neilson D and Choptuik M 2000 {\it Class. Quantum Grav.} {\bf 17} 761 (arXiv:gr-qc/9812053)
\item Sundu H, Azizi K, S\"ung\"u J Y and Yinelek N 2013 Properties of $D_{s2}^*(2573)$ charmed-strange tensor meson arXiv:1307.6058
\endnumrefs

\noindent For preprints added to arXiv.org after April 2007 it is not necessary to include the subject area, however this information can be included in square brackets after the number if desired, e.g.
\numrefs{1}
\item Sundu H, Azizi K, S\"ung\"u J Y and Yinelek N 2013 Properties of $D_{s2}^*(2573)$ charmed-strange tensor meson arXiv:1307.6058 [hep-ph]
\endnumrefs

\subsection{References to books, conference proceedings and reports}

References to books, proceedings and reports are similar, but have only two
changes of font. The authors and date of publication are in Roman, the
title of the book is in italic, and the editors, publisher,
town of publication
and page number are in Roman. A typical reference to a book and a
conference paper might be

\smallskip
\begin{harvard}
\item[] Dorman L I 1975 {\it Variations of Galactic Cosmic Rays}
(Moscow: Moscow State University Press) p~103
\item[] Caplar R and Kulisic P 1973 {\it Proc.\
Int.\ Conf.\ on Nuclear Physics (Munich)} vol~1 (Amsterdam:
North-Holland/American Elsevier) p~517
\end{harvard}
\smallskip

\noindent which would be obtained by with the code
\small\begin{verbatim}
\item[] Dorman L I 1975 {\it Variations of Galactic Cosmic Rays}
(Moscow: Moscow State University Press) p~103
\item[] Caplar R and Kulisic P 1973 {\it Proc. Int. Conf. on Nuclear
Physics (Munich)} vol~1 (Amsterdam: North-Holland/American
Elsevier) p~517
\end{verbatim}\normalsize
\noindent

\noindent Features to note are the following.
\begin{enumerate}
\item Book titles are in italic and should be spelt out in full with
initial capital letters for all except minor words. Words such as
Proceedings, Symposium, International, Conference, Second, etc should
be abbreviated to Proc., Symp., Int., Conf., 2nd,
respectively, but the rest of the title should be given in full,
followed by the date of the conference and the
town or city where the conference was held. For
laboratory reports the laboratory should be spelt out wherever
possible, e.g.\ {\it Argonne National Laboratory Report}.

\item The volume number, for example, vol~2, should be followed by
the editors, if any, in the form ed~A~J~Smith and P~R~Jones. Use
\etal if there are more than two editors. Next comes the town of
publication and publisher, within brackets and separated by a colon,
and finally the page numbers preceded by p if only one number is given
or pp if both the initial and final numbers are given.

\item If a book is part of a series (for examples, {\it Springer Tracts in Modern Physics\/}), the series title and volume number is given in parentheses after the book title. Whereas for an individual volume in a multivolume set, the set title is given first, then the volume title.
\end{enumerate}
\smallskip
\begin{harvard}
\item[]Morse M 1996 Supersonic beam sources {\it Atomic Molecular and Optical Physics\/} ({\it Experimental Methods in the Physical Sciences\/} vol 29) ed F B Dunning and R Hulet (San Diego, CA: Academic)
\item[]Fulco C E, Liverman C T and Sox H C (eds) 2000 {\it Gulf War and Health\/} vol 1 {\it Depleted Uranium, Pyridostigmine Bromide, Sarin, and Vaccines\/} (Washington, DC: The National Academies Press)
\end{harvard}

\section{Cross-referencing\label{xrefs}}
The facility to cross reference items in the text is very useful when
composing articles as the precise form of the article may be uncertain at the start
and  revisions and amendments may subsequently be made.
\LaTeX\ provides excellent facilities for doing cross-referencing
and these can be very useful in preparing articles.

\subsection{References}
\label{refs}
Cross referencing is useful for numeric reference lists because, if it
is used, adding
another reference to the list does not then involve renumbering all
subsequent references. It is not necessary for referencing
in the Harvard system where the final reference list is alphabetical
and normally no other changes are necessary when a reference is added or
deleted.
When using \LaTeX , two passes (under certain circumstances, three passes)
are necessary initially to get the cross references right
but once they are correct a single run is usually sufficient provided an
\verb".aux" file is available and the file
is run to the end each time.
If the
reference list contains an entry \verb"\bibitem{label}",
this command
will produce the correct number in the reference list and
\verb"\cite{label}" will produce the number within square brackets in the
text. \verb"label" may contain letters, numbers
or punctuation characters but must not contain spaces or commas. It is also
recommended that the underscore character \_{} is not used in cross
referencing.
Thus labels of the form
\verb"eq:partial", \verb"fig:run1", \verb"eq:dy'",
etc, may be used. When several
references occur together in the text \verb"\cite" may be used with
multiple labels with commas but no spaces separating them;
the output will be the
numbers within a single pair of square brackets with a comma and a
thin space separating the numbers. Thus \verb"\cite{label1,label2,label4}"
would give [1,\,2,\,4]. Note that no attempt is made by the style file to sort the
labels and no shortening of groups of consecutive numbers is done.
Authors should therefore either try to use multiple labels in the correct
order, or use a package such as \verb"cite.sty" that reorders labels
correctly.

The numbers for the cross referencing are generated in the order the
references appear in the reference list, so that if the entries in the
list are not in the order in which the references appear in the text
then the
numbering within the text will not be sequential. To correct this
change the ordering of the entries in the reference list and then
rerun the \LaTeX\ file {\it twice}.  Please ensure that all references resolve correctly: check the \verb".log" file
for undefined or multiply-defined citations, and check that the output does not contain question
marks that indicate unresolved references.

\subsection{Equation numbers, sections, subsections, figures and
tables}
Labels for equation numbers, sections, subsections, figures and tables
are all defined with the \verb"\label{label}" command and cross references
to them are made with the \verb"\ref{label}" command.

Any section, subsection, subsubsection, appendix or subappendix
command defines a section type label, e.g. 1, 2.2, A2, A1.2 depending
on context. A typical article might have in the code of its introduction
`The results are discussed in section\verb"~\ref{disc}".' and
the heading for the discussion section would be:
\small\begin{verbatim}
\section{Results}\label{disc}
\end{verbatim}\normalsize
Labels to sections, etc, may occur anywhere within that section except
within another numbered environment.
Within a maths environment labels can be used to tag equations which are
referred to within the text.

In addition to the standard \verb"\ref{<label>}", in \verb"iopart.cls" the abbreviated
forms given in \tref{abrefs}
are available for reference to standard parts of the text.

\Table{\label{abrefs}Alternatives to the normal references command {\tt $\backslash$ref} available in {\tt iopart.cls},
and the text generated by
them. Note it is not normally necessary to include the word equation
before an equation number except where the number starts a sentence. The
versions producing an initial capital should only be used at the start of
sentences.}
\br
Reference&Text produced\\
\mr
\verb"\eref{<label>}"&(\verb"<num>")\\
\verb"\Eref{<label>}"&Equation (\verb"<num>")\\
\verb"\fref{<label>}"&figure \verb"<num>"\\
\verb"\Fref{<label>}"&Figure \verb"<num>"\\
\verb"\sref{<label>}"&section \verb"<num>"\\
\verb"\Sref{<label>}"&Section \verb"<num>"\\
\verb"\tref{<label>}"&table \verb"<num>"\\
\verb"\Tref{<label>}"&Table \verb"<num>"\\
\br
\endTable

\section{Tables and table captions}
Tables are numbered serially and referred to in the text
by number (table 1, etc, {\bf not} tab. 1). Each table should have an
explanatory caption which should be as concise as possible. If a table
is divided into parts these should be labelled \pt(a), \pt(b),
\pt(c), etc but there should be only one caption for the whole
table, not separate ones for each part.

In the preprint style the tables may be included in the text
or listed separately after the reference list
starting on a new page.

\subsection{The basic table format}
The standard form for a table in \verb"iopart.cls" is:
\small\begin{verbatim}
\begin{table}
\caption{\label{label}Table caption.}
\begin{indented}
\item[]\begin{tabular}{@{}llll}
\br
Head 1&Head 2&Head 3&Head 4\\
\mr
1.1&1.2&1.3&1.4\\
2.1&2.2&2.3&2.4\\
\br
\end{tabular}
\end{indented}
\end{table}
\end{verbatim}\normalsize

\noindent Points to note are:
\begin{enumerate}
\item The caption comes before the table. It should have a period at
the end.

\item Tables are normally set in a smaller type than the text.
The normal style is for tables to be indented. This is accomplished
by using \verb"\begin{indented}" \dots\ \verb"\end{indented}"
and putting \verb"\item[]" before the start of the tabular environment.
Omit these
commands for any tables which will not fit on the page when indented.

\item The default is for columns to be aligned left and
adding \verb"@{}" omits the extra space before the first column.

\item Tables have only horizontal rules and no vertical ones. The rules at
the top and bottom are thicker than internal rules and are set with
\verb"\br" (bold rule).
The rule separating the headings from the entries is set with
\verb"\mr" (medium rule).  These are special \verb"iopart.cls" commands.

\item Numbers in columns should be aligned on the decimal point;
to help do this a control sequence \verb"\lineup" has been defined
in \verb"iopart.cls"
which sets \verb"\0" equal to a space the size of a digit, \verb"\m"
to be a space the width of a minus sign, and \verb"\-" to be a left
overlapping minus sign. \verb"\-" is for use in text mode while the other
two commands may be used in maths or text.
(\verb"\lineup" should only be used within a table
environment after the caption so that \verb"\-" has its normal meaning
elsewhere.) See table~\ref{tabone} for an example of a table where
\verb"\lineup" has been used.
\end{enumerate}

\begin{table}
\caption{\label{tabone}A simple example produced using the standard table commands
and $\backslash${\tt lineup} to assist in aligning columns on the
decimal point. The width of the
table and rules is set automatically by the
preamble.}

\begin{indented}
\lineup
\item[]\begin{tabular}{@{}*{7}{l}}
\br
$\0\0A$&$B$&$C$&\m$D$&\m$E$&$F$&$\0G$\cr
\mr
\0\023.5&60  &0.53&$-20.2$&$-0.22$ &\01.7&\014.5\cr
\0\039.7&\-60&0.74&$-51.9$&$-0.208$&47.2 &146\cr
\0123.7 &\00 &0.75&$-57.2$&\m---   &---  &---\cr
3241.56 &60  &0.60&$-48.1$&$-0.29$ &41   &\015\cr
\br
\end{tabular}
\end{indented}
\end{table}

\subsection{Simplified coding and extra features for tables}
The basic coding format can be simplified using extra commands provided in
the \verb"iopart" class file. The commands up to and including
the start of the tabular environment
can be replaced by
\small\begin{verbatim}
\Table{\label{label}Table caption}
\end{verbatim}\normalsize
and this also activates the definitions within \verb"\lineup".
The final three lines can also be reduced to \verb"\endTable" or
\verb"\endtab". Similarly for a table which does not fit on the page when indented
\verb"\fulltable{\label{label}caption}" \dots\ \verb"\endfulltable"
can be used. \LaTeX\ optional positional parameters can, if desired, be added after
\verb"\Table{\label{label}caption}" and \verb"\fulltable{\label{label}caption}".

\verb"\centre{#1}{#2}" can be used to centre a heading
\verb"#2" over \verb"#1"
columns and \verb"\crule{#1}" puts a rule across
\verb"#1" columns. A negative
space \verb"\ns" is usually useful to reduce the space between a centred
heading and a centred rule. \verb"\ns" should occur immediately after the
\verb"\\" of the row containing the centred heading (see code for
\tref{tabl3}). A small space can be
inserted between rows of the table
with \verb"\ms" and a half line space with \verb"\bs"
(both must follow a \verb"\\" but should not have a
\verb"\\" following them).

\Table{\label{tabl3}A table with headings spanning two columns and containing notes.
To improve the
visual effect a negative skip ($\backslash${\tt ns})
has been put in between the lines of the
headings. Commands set-up by $\backslash${\tt lineup} are used to aid
alignment in columns. $\backslash${\tt lineup} is defined within
the $\backslash${\tt Table} definition.}
\br
&&&\centre{2}{Separation energies}\\
\ns
&Thickness&&\crule{2}\\
Nucleus&(mg\,cm$^{-2}$)&Composition&$\gamma$, n (MeV)&$\gamma$, 2n (MeV)\\
\mr
$^{181}$Ta&$19.3\0\pm 0.1^{\rm a}$&Natural&7.6&14.2\\
$^{208}$Pb&$\03.8\0\pm 0.8^{\rm b}$&99\%\ enriched&7.4&14.1\\
$^{209}$Bi&$\02.86\pm 0.01^{\rm b}$&Natural&7.5&14.4\\
\br
\end{tabular}
\item[] $^{\rm a}$ Self-supporting.
\item[] $^{\rm b}$ Deposited over Al backing.
\end{indented}
\end{table}

Units should not normally be given within the body of a table but
given in brackets following the column heading; however, they can be
included in the caption for long column headings or complicated units.
Where possible tables should not be broken over pages.
If a table has related notes these should appear directly below the table
rather than at the bottom of the page. Notes can be designated with
footnote symbols (preferable when there are only a few notes) or
superscripted small roman letters. The notes are set to the same width as
the table and in normal tables follow after \verb"\end{tabular}", each
note preceded by \verb"\item[]". For a full width table \verb"\noindent"
should precede the note rather than \verb"\item[]". To simplify the coding
\verb"\tabnotes" can, if desired, replace \verb"\end{tabular}" and
\verb"\endtabnotes" replaces
\verb"\end{indented}\end{table}".

If all the tables are grouped at the end of a document
the command \verb"\Tables" is used to start a new page and
set a heading `Tables and table captions'. If the tables follow an appendix then add the command \verb"\noappendix" to revert to normal style numbering.

\section{Figures and figure captions}

Figures (with their captions) can be incorporated into the text at the appropriate position or grouped together
at the end of the article. If the figures are at the end of the article and follow an appendix then in \verb"iopart.cls" you can add the command \verb"\noappendix" to revert to normal style numbering.  We remind you that you must seek permission
to reuse any previously-published figures, and acknowledge their use correctly---see section \ref{copyright}.

\subsection{Inclusion of graphics files\label{figinc}}
Using the \verb"graphicx" package graphics files can
be included within figure and center environments at an
appropriate point within the text using code such as:
\small\begin{verbatim}

\end{verbatim}\normalsize
The \verb"graphicx" package supports various optional arguments
to control the appearance of the figure. Other similar
packages can also be used (e.g. \verb"graphics", \verb"epsf").   Whatever package you use,
you must include it explicitly after the \verb"\documentclass" declaration using (say)
\verb"\usepackage{graphicx}".

For more detail about graphics inclusion see the documentation
of the \verb"graphicx" package, refer to one of the books on \LaTeX , e.g. Goosens M, Rahtz S and Mittelbach F 1997 {\it The }\LaTeX\ {\it Graphics Companion\/}
(Reading, MA: Addison-Wesley),
or download some of the excellent free documentation available via the Comprehensive
TeX Archive Network (CTAN) \verb"http://www.ctan.org"---{in particular see Reckdahl K 2006 {\it Using Imported Graphics in }\LaTeX\ {\it and }pdf\LaTeX\ \verb"http://www.ctan.org/tex-archive/info/epslatex".

IOP Publishing's graphics guidelines provide further information on preparing \verb".eps" files.

We prefer you to use \verb".eps" files for your graphics, but we realise that converting other
formats of graphics to \verb".eps" format can be troublesome.  If you use PDF or bitmap-format graphics
such as JPG or PNG that need to be included using the pdf\TeX\ package, this is OK, but please bear
in mind that the PDF you submit should use PDF standard 1.4 or lower (use \verb"\pdfminorversion=4" at the
start of the file).

The main \LaTeX\ file must read in graphics files and subsidiary \LaTeX\ files from the current directory,
{\it not} from a subdirectory.  Your submission files are stored on our systems in a single location and we will not be able to process your
TeX file automatically if it relies on organization of the files into subdirectories.

\subsection{Captions}
Below each figure should be a brief caption describing it and, if
necessary, interpreting the various lines and symbols on the figure.
As much lettering as possible should be removed from the figure itself
and included in the caption. If a figure has parts, these should be
labelled ($a$), ($b$), ($c$), etc and all parts should be described
within a single caption. \Tref{blobs} gives the definitions for describing
symbols and lines often used within figure captions (more symbols are
available when using the optional packages loading the AMS extension fonts).

\subsection{Supplementary Data}
All of our journals encourage authors to submit supplementary data attachments to
enhance the online versions of published research articles. Supplementary data
enhancements typically consist of video clips, animations or
data files, tables of extra information or extra figures. They can
add to the reader's understanding and present results in attractive ways that go
beyond what can be presented in the PDF version of the article.
See our supplementary data guidelines for further details.

Software, in the form of input scripts for mathematical packages (such as Mathematica notebook files), or
source code that can be interpreted or compiled (such as Python scripts or Fortran or C programs), or executable
files, can sometimes be accepted as supplementary data, but the journal may ask you for assurances about
the software and distribute them from the article web page only subject to a disclaimer.  Contact the journal
in the first instance if you want to submit software.

\begin{table}[t]
\caption{\label{blobs}Control sequences to describe lines and symbols in figure
captions.}
\begin{indented}
\item[]\begin{tabular}{@{}lllll}
\br
Control sequence&Output&&Control sequence&Output\\
\mr
\verb"\dotted"&\dotted        &&\verb"\opencircle"&\opencircle\\
\verb"\dashed"&\dashed        &&\verb"\opentriangle"&\opentriangle\\
\verb"\broken"&\broken&&\verb"\opentriangledown"&\opentriangledown\\
\verb"\longbroken"&\longbroken&&\verb"\fullsquare"&\fullsquare\\
\verb"\chain"&\chain          &&\verb"\opensquare"&\opensquare\\
\verb"\dashddot"&\dashddot    &&\verb"\fullcircle"&\fullcircle\\
\verb"\full"&\full            &&\verb"\opendiamond"&\opendiamond\\
\br
\end{tabular}
\end{indented}
\end{table}

\clearpage

\appendix

\section{List of macros for formatting text, figures and tables}

\begin{table}[hb]
\caption{Macros available for use in text in {\tt iopart.cls}. Parameters in square brackets are optional.}
\footnotesize\rm
\begin{tabular}{@{}*{7}{l}}
\br
Macro name&Purpose\\
\mr
\verb"\title[#1]{#2}"&Title of article and short title (optional)\\
\verb"\paper[#1]{#2}"&Title of paper and short title (optional)\\
\verb"\letter{#1}"&Title of Letter to the Editor\\
\verb"\ftc{#1}"&Title of Fast Track Communication\\
\verb"\rapid[#1]{#2}"&Title of Rapid Communication and short title (optional)\\
\verb"\comment[#1]{#2}"&Title of Comment and short title (optional)\\
\verb"\topical[#1]{#2}"&Title of Topical Review and short title
(optional)\\
\verb"\review[#1]{#2}"&Title of review article and short title (optional)\\
\verb"\note[#1]{#2}"&Title of Note and short title (optional)\\
\verb"\prelim[#1]{#2}"&Title of Preliminary Communication \& short title\\
\verb"\author{#1}"&List of all authors\\
\verb"\article[#1]{#2}{#3}"&Type and title of other articles and
short title (optional)\\
\verb"\address{#1}"&Address of author\\
\verb"\ams{#1}"&Mathematics Classification Scheme\\
\verb"\submitto{#1}"&`Submitted to' message\\
\verb"\maketitle"&Creates title page\\
\verb"\begin{abstract}"&Start of abstract\\
\verb"\end{abstract}"&End of abstract\\
\verb"\nosections"&Inserts space before text when no sections\\
\verb"\section{#1}"&Section heading\\
\verb"\subsection{#1}"&Subsection heading\\
\verb"\subsubsection{#1}"&Subsubsection heading\\
\verb"\appendix"&Start of appendixes\\
\verb"\ack"&Acknowledgments heading\\
\verb"\References"&Heading for reference list\\
\verb"\begin{harvard}"&Start of alphabetic reference list\\
\verb"\end{harvard}"&End of alphabetic reference list\\
\verb"\begin{thebibliography}{#1}"&Start of numeric reference list\\
\verb"\end{thebibliography}"&End of numeric reference list\\
\verb"\etal"&\etal for text and reference lists\\
\verb"\nonum"&Unnumbered entry in numerical reference list\\
\br
\end{tabular}
\end{table}

\clearpage

\begin{table}
\caption{Macros defined within {\tt iopart.cls}
for use with figures and tables.}
\begin{indented}
\item[]\begin{tabular}{@{}l*{15}{l}}
\br
Macro name&Purpose\\
\mr
\verb"\Figures"&Heading for list of figure captions\\
\verb"\Figure{#1}"&Figure caption\\
\verb"\Tables"&Heading for tables and table captions\\
\verb"\Table{#1}"&Table caption\\
\verb"\fulltable{#1}"&Table caption for full width table\\
\verb"\endTable"&End of table created with \verb"\Table"\\
\verb"\endfulltab"&End of table created with \verb"\fulltable"\\
\verb"\endtab"&End of table\\
\verb"\br"&Bold rule for tables\\
\verb"\mr"&Medium rule for tables\\
\verb"\ns"&Small negative space for use in table\\
\verb"\centre{#1}{#2}"&Centre heading over columns\\
\verb"\crule{#1}"&Centre rule over columns\\
\verb"\lineup"&Set macros for alignment in columns\\
\verb"\m"&Space equal to width of minus sign\\
\verb"\-"&Left overhanging minus sign\\
\verb"\0"&Space equal to width of a digit\\
\br
\end{tabular}
\end{indented}
\end{table}

\clearpage

\begin{table}[hb]
\caption{\label{jlab2}Abbreviations in {\tt iopart.cls} for journals handled by IOP Publishing.}
\footnotesize
\begin{tabular}{@{}llll}
\br
{\rm Short form of journal title} & Macro & {\rm Short form of journal title} & Macro \\
\mr
2D Mater.&\verb"\TDM"&J. Radiol. Prot.&\verb"\JRP"\\
AJ&\verb"\AJ"&J. Semicond.&\verb"\JOS"\\
ApJ&\verb"\APJ"&J. Stat. Mech.&\verb"\JSTAT"\\
ApJL&\verb"\APJL"&Laser Phys.&\verb"\LP"\\
ApJS&\verb"\APJS"&Laser Phys. Lett.&\verb"\LPL"\\
Adv. Nat. Sci: Nanosci. Nanotechnol.&\verb"\ANSN"&Metrologia&\verb"\MET"\\
Appl. Phys. Express&\verb"\APEX"&Mater. Res. Express&\verb"\MRE"\\
Biofabrication&\verb"\BF"&Meas. Sci. Technol.&\verb"\MST"\\
Bioinspir. Biomim.&\verb"\BB"&Methods Appl. Fluoresc.&\verb"\MAF"\\
Biomed. Mater.&\verb"\BMM"&Modelling Simul. Mater. Sci. Eng.&\verb"\MSMSE"\\
Chin. J. Chem. Phys.&\verb"\CJCP"&Nucl. Fusion&\verb"\NF"\\
Chinese Phys. B&\verb"\CPB"&New J. Phys.&\verb"\NJP"\\
Chinese Phys. C&\verb"\CPC"&Nonlinearity&\verb"\NL"\\
Chinese Phys. Lett.&\verb"\CPL"&Nanotechnology&\verb"\NT"\\
Class. Quantum Grav.&\verb"\CQG"&Phys. Biol.&\verb"\PB"\\
Commun. Theor. Phys.&\verb"\CTP"&Phys. Educ.&\verb"\PED"\\
Comput. Sci. Disc.&\verb"\CSD"&Phys.-Usp.&\verb"\PHU"\\
Environ. Res. Lett.&\verb"\ERL"&Physiol. Meas.&\verb"\PM"\\
EPL&\verb"\EPL"&Phys. Med. Biol.&\verb"\PMB"\\
Eur. J. Phys.&\verb"\EJP"&Phys. Scr.&\verb"\PS"\\
Fluid Dyn. Res.&\verb"\FDR"&Plasma Phys. Control. Fusion&\verb"\PPCF"\\
Inverse Problems&\verb"\IP"&Plasma Sci. Technol.&\verb"\PST"\\
Izv. Math.&\verb"\IZV"&Plasma Sources Sci. Technol.&\verb"\PSST"\\
Jpn. J. Appl. Phys.&\verb"\JJAP"&Quantum Electron.&\verb"\QEL"\\
J. Breath Res.&\verb"\JBR"&Rep. Prog. Phys.&\verb"\RPP"\\
JCAP&\verb"\JCAP"&Res. Astron. Astrophys.&\verb"\RAA"\\
J. Geophys. Eng.&\verb"\JGE"&Russ. Chem. Rev.&\verb"\RCR"\\
JINST&\verb"\JINST"&Russ. Math. Surv.&\verb"\RMS"\\
J. Micromech. Microeng.&\verb"\JMM"&Sb. Math.&\verb"\MSB"\\
J. Neural Eng.&\verb"\JNE"&Science Foundation in China&\verb"\SFC"\\
J. Opt.&\verb"\JOPT"&Sci. Technol. Adv. Mater.&\verb"\STAM"\\
J. Phys. A: Math. Theor.&\verb"\jpa"&Semicond. Sci. Technol.&\verb"\SST"\\
J. Phys. B: At. Mol. Opt. Phys.&\verb"\jpb"&Smart Mater. Struct.&\verb"\SMS"\\
J. Phys: Condens. Matter&\verb"\JPCM"&Supercond. Sci. Technol.&\verb"\SUST"\\
J. Phys. D: Appl. Phys.&\verb"\JPD"&Surf. Topogr.: Metrol. Prop.&\verb"\STMP"\\
J. Phys. G: Nucl. Part. Phys.&\verb"\jpg"&Transl. Mater. Res.&\verb"\TMR"\\
\mr
{\it IOP Conference Series journals}\\
\mr
J. Phys.: Conf. Ser.&\verb"\JPCS"\\
IOP Conf. Ser.: Earth Environ. Sci.&\verb"\EES"\\
IOP Conf. Ser.: Mater. Sci. Eng.&\verb"\MSE"\\

\br
\end{tabular}

\end{table}

\clearpage

\begin{table}

\caption{\label{jlab2b}Abbreviations for IOP Publishing journals that are no longer published.}
\begin{indented}
\item[]\begin{tabular}{@{}lll}
\br
{\rm Short form of journal title} & Macro name & Years relevant\\
\mr
J. Phys. A: Math. Gen.&\verb"\JPA"&1975--2006\\
J. Phys. B: At. Mol. Phys.&\verb"\JPB"&1968--1987\\
J. Phys. C: Solid State Phys.&\verb"\JPC"&1968--1988\\
J. Phys. E: Sci. Instrum.&\verb"\JPE"&1968--1989\\
J. Phys. F: Met. Phys.&\verb"\JPF"&1971--1988\\
J. Phys. G: Nucl. Phys.&\verb"\JPG"&1975--1988\\
Pure Appl. Opt.&\verb"\PAO"&1992--1998\\
Quantum Opt.&\verb"\QO"&1989--1994\\
Quantum Semiclass. Opt.&\verb"\QSO"&1995--1998\\
J. Opt. A: Pure Appl. Opt.&\verb"\JOA"&1999--2009\\
J. Opt. B: Quantum Semiclass. Opt.&\verb"\JOB"&1999--2005\\
\br
\end{tabular}
\end{indented}
\end{table}

\begin{table}[h]

\caption{\label{jlab3}Abbreviations in {\tt iopart.cls} for some
common journals not handled by IOP Publishing.}
\begin{indented}
\item[]\begin{tabular}{@{}llll}
\br
Short form of journal & Macro & Short form of Journal & Macro\\
\mr
Acta Crystallogr.&\verb"\AC"&J. Quant. Spectrosc. Radiat. Transfer&\verb"\JQSRT"\\
Acta Metall.&\verb"\AM"&Nuovo Cimento&\verb"\NC"\\
Ann. Phys., Lpz&\verb"\AP"&Nucl. Instrum. Methods&\verb"\NIM"\\
Ann. Phys., NY&\verb"\APNY"&Nucl. Phys.&\verb"\NP"\\
Ann. Phys., Paris&\verb"\APP"&Phys. Fluids&\verb"\PF"\\
Can. J. Phys.&\verb"\CJP"&Phys. Lett.&\verb"\PL"\\
Gen. Rel. Grav.&\verb"\GRG"&Phys. Rev.&\verb"\PR"\\
J. Appl. Phys.&\verb"\JAP"&Phys. Rev. Lett.&\verb"\PRL"\\
J. Chem. Phys.&\verb"\JCP"&Proc. R. Soc.&\verb"\PRS"\\
J. High Energy Phys.&\verb"\JHEP"&Phys. Status Solidi&\verb"\PSS"\\
J. Magn. Magn. Mater.&\verb"\JMMM"&Phil. Trans. R. Soc.&\verb"\PTRS"\\
J. Math. Phys.&\verb"\JMP"&Rev. Mod. Phys.&\verb"\RMP"\\
J. Opt. Soc. Am.&\verb"\JOSA"&Rev. Sci. Instrum.&\verb"\RSI"\\
J. Physique&\verb"\JP"&Solid State Commun.&\verb"\SSC"\\
J. Phys. Chem.&\verb"\JPhCh"&Sov. Phys.--JETP&\verb"\SPJ"\\
J. Phys. Soc. Jpn.&\verb"\JPSJ"&Z. Phys.&\verb"\ZP"\\

\br
\end{tabular}
\end{indented}
\end{table}

\clearpage

\section{Including author names using Chinese, Japanese and Korean characters in submissions to IOP Publishing journals}
Authors in all IOP Publishing journals have the option to include names in Chinese, Japanese or Korean (CJK) characters in addition to the English name. The names will be displayed in the print issue and the online PDF, abstract and table of contents, in parentheses after the English name.

It is the decision of the individual authors whether or not to include a CJK version of their names; for a single article it is not necessary for all authors to include a CJK name if only one author wishes to do so. It is the responsibility of the authors to check the accuracy and formatting of the names in the final proofs that they receive prior to publication.

To include names in CJK characters, authors should use the \verb"cjk.sty" package, available from \verb"http://www.ctan.org/tex-archive/language/chinese/CJK/". Users should be aware that this is a very large and complicated package which relies on a large number of fonts.  We recommend using a TeX package that includes this package and all of the fonts by default, so that manual configuration is not required (e.g. the TeXLive distribution, which is available on all platforms (Macintosh, Windows and Linux)).

The documentation for the \verb"cjk.sty" package gives information on how CJK characters can be included in TeX files.  Most authors will find it convenient to include the characters in one of the standard encodings such as UTF-8, GB or JIS, if they have access to a text editor that supports such encodings.

Example TeX coding might be:
\begin{verbatim}
\documentclass[12pt]{iopart}
\usepackage{CJK}
.
.
.
\begin{document}
\begin{CJK*}{GBK}{ }

\title[]{Title of article}
\author{Author Name (CJK characters)}
\address{Department, University, City, Country}
.
.
.
\end{CJK*}
\end{verbatim}

To avoid potential problems in handling the CJK characters in submissions, authors should always include a PDF of the full version of their papers (including all figure files, tables, references etc) with the CJK characters in it.

\end{document}

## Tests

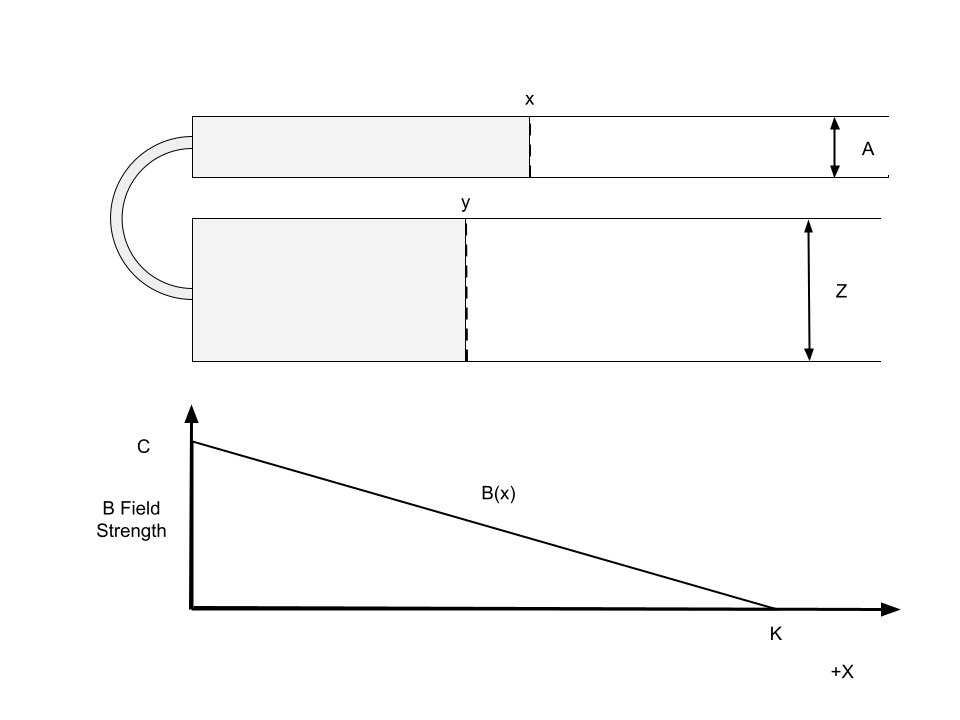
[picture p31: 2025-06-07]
doc/EnergyMinimization/figure/ThoughtExperiment.png

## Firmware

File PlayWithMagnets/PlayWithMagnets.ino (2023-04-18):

/*
 * Copyright Robert L. Read, 2022
 * PlayWithMagnets
 * A program to manipulate digital pins to contol tranistors to gate power 
 * to magnets
 * Released by Public Invention under GNU Affero License
 */

// The simplest thing is to have a single "on" period for each magnet
// and then oscillate through the magnets
const long DURATION_ON_MS = 400;
const int OVERLAP = 200;


const int NUM_MAGNETS = 4;
int MAGNET_PIN[NUM_MAGNETS];

// This the TOTAL period of an ascending cycle and then a descending cycle.
const long HALF_PERIOD_MS = NUM_MAGNETS * DURATION_ON_MS;
const long PERIOD_MS = 2 * HALF_PERIOD_MS;

void init_pins() {
 // for(int i = 0; i < NUM_MAGNETS; i++) {
 int i;
  i = 0;
  MAGNET_PIN[i] = 2+1;
  pinMode(MAGNET_PIN[i], OUTPUT);
  digitalWrite(MAGNET_PIN[i],LOW);

  i = 1;
  MAGNET_PIN[i] = 2+3;
  pinMode(MAGNET_PIN[i], OUTPUT);
  digitalWrite(MAGNET_PIN[i],LOW);

  i = 2;
  MAGNET_PIN[i] = 2+2;
  pinMode(MAGNET_PIN[i], OUTPUT);
  digitalWrite(MAGNET_PIN[i],LOW);

  i = 3;
  MAGNET_PIN[i] = 2+0;
  pinMode(MAGNET_PIN[i], OUTPUT);
  digitalWrite(MAGNET_PIN[i],LOW);
 // }
}

void setup() {
  // put your setup code here, to run once:
  init_pins();
  Serial.begin(9600);
  delay(1000);
  
}

// At first I'm just going to turn the magnet on with a duty cycle
// to see if I can jiggle the ferrofluid and keep the coils cool
// overlap is the time to leave both magnets on.
void set_mag_as_radio_button(int mag,int overlap) {
  for(int i = 0; i < NUM_MAGNETS; i++) {
    if (mag == i) {
     digitalWrite(MAGNET_PIN[i],HIGH);
    }
  }
  delay(overlap);
  for(int i = 0; i < NUM_MAGNETS; i++) {
     if (mag != i) {
      digitalWrite(MAGNET_PIN[i],LOW);
     }
  }
}

void loop() {
  // put your main code here, to run repeatedly:
  delay(DURATION_ON_MS / 2);
  long ms = millis();
  int lms = (ms % PERIOD_MS);

  // We want to turn the magnets on in ascending order and then descending order.
  // Perhaps the easiest way to do this is test the current time modulo the number
  // times the period times two to determine first if we are descending or ascending,
  // and then which magnet we are on.
  int magnet_order;
  if (lms < (HALF_PERIOD_MS)) { // ascending
    magnet_order = lms / DURATION_ON_MS;   
  } else { // descending
    lms = lms - HALF_PERIOD_MS;
    magnet_order = (NUM_MAGNETS - 1) - (lms / DURATION_ON_MS);
  }
  Serial.print("magnet on:");
  Serial.println(magnet_order);
  set_mag_as_radio_button(magnet_order,OVERLAP);
}

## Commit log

2017-08-09 adding a new diagram of laser cutting design
2021-11-23 adding models
    [FerrofluidModel.SLDPRT, FerrofluidModel.STL]
2021-12-18 adding experimental pump apparatus
    [PumpConceptV0.1.scad, PumpConceptV0.1.stl]
2022-05-01 update with new pump model from Veronica
    [Ferrofluid Pump Electromagnets.SLDPRT, PumpConceptV0.2.scad, PumpConceptV0.2.stl]
2024-01-09 Update asme2ej.tex
    check valve mth
2024-01-13 fixing problems
    [ImprovedCheckValveV2.stl]
2024-01-14 improving the paper
    [ImprovedCheckValve.scad, ImprovedCheckValve.stl, ImprovedCheckValveV2.stl]
2024-01-22 changing to using barb fittings
    [ImprovedCheckValve3.stl]
2024-02-27 update of the model and some minor tweaks
    [ImprovedCheckValve.scad]
2024-03-11 adding the High Chamber concept
    [HighChamber.stl, ImprovedCheckValve.scad]
2024-03-25 improved check valve
    [HighChamber.stl, ImprovedCheckValve.scad]
2024-04-09 new valve designs
    [AirGapValve.stl, HighChamber.stl, ImprovedCheckValve.scad]
2024-04-09 updating main file
    [ImprovedCheckValve.scad]
2024-05-14 proved, I think, that you can make an asymmetric valve.
2024-06-04 attempting to repair the valves
    [AirGapValve.stl, HighChamber.stl, ImprovedCheckValve.scad]
2024-06-10 repairing valve
    [AirGapValve.stl, HighChamber.stl, ImprovedCheckValve.scad]
2024-07-28 added a theory to valves in series

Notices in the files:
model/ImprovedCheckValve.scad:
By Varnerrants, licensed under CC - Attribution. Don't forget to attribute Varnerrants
